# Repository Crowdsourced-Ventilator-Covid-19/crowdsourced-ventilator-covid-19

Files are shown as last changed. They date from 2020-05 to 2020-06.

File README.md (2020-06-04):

# crowdsourced-ventilator-covid-19
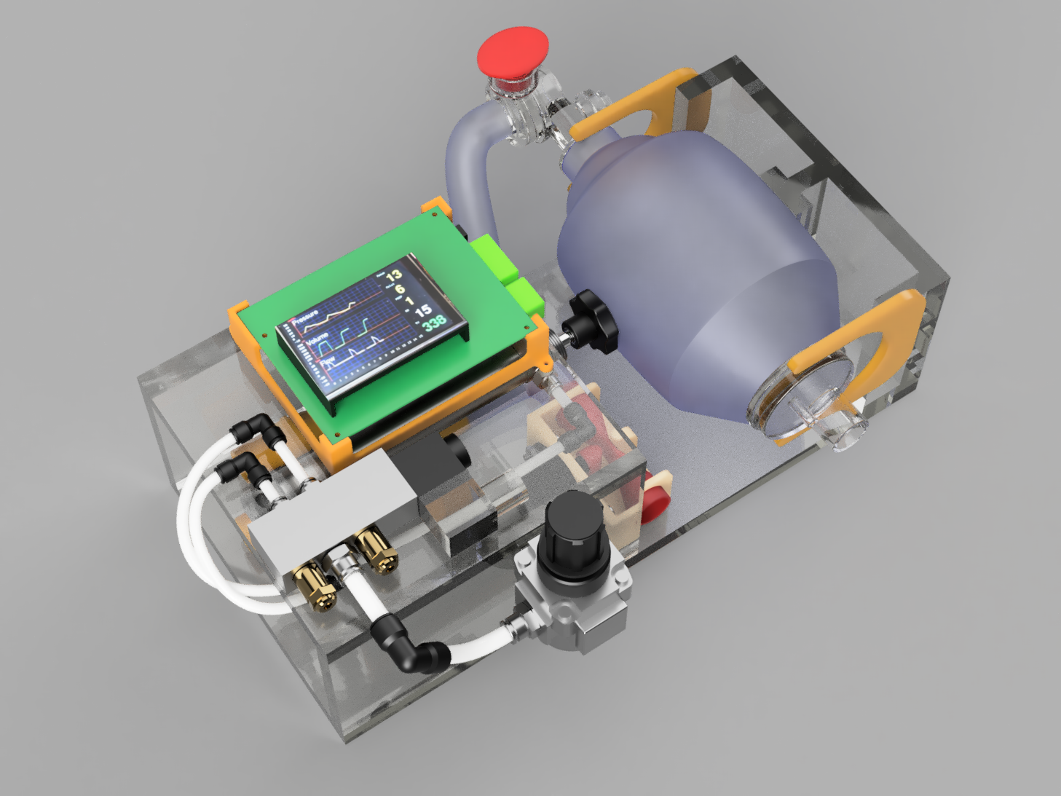
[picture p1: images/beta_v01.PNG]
beta render

## Problem Statement
How to create a safe ventilator that can be used as a last resort where a physician has no choice but to use it or lose a life.  Obviously it will not be FDA approved.  In fact, a wonderful outcome would be if somehow US industry could step up to solve the problem of the ventilator shortage.  However, based on the data we are seeing from Johns Hopkins site above it is likely by the time industry succeeds thousand of people may be in respiratory distress,  particularly in New York City and other big hot spots.  So far no deaths in MA but statistically speaking this will not last for long.

Can we make a difference?
> Honestly I am not sure we can,  but we can try to help, even if we save one life long enough to get on a commercially available ventilator.  In my religion, it is said that saving one life saves an entire world.
-- Joe Siegel

So can we design a ventilator good enough to help and do no harm to the patient?   Can this design be simple enough to put together from components readily available on Amazon or hobby shops or any place that can source the components.  Can we crowd source the production of this design and the cost to build it.  If it can be simple, crowd sourced and done quickly we might be able to help.  The other option is to take the design to someone who will put them into production until the Medical Industrial Complex takes over.

## Team
1. Joe Siegel - Electrical/Physics Engineer  Advanced Micro Devices
1. Steve Bunes - Engineer/Physics and CEO Rise Time Inc. Chicago
1. Chuck Tung - Electrical Engineer / Mechanical Engineer Advanced Micro Devices
1. Dr. David Kagle - Anesthesiologist Emerson Hospital
1. Kenny House - Biomedical Engineer and currently works for AMD 

## Resources
### Specs
- [UK Rapidly Manufactured Ventilator Spec](https://www.gov.uk/government/publications/coronavirus-covid-19-ventilator-supply-specification/rapidly-manufactured-ventilator-system-specification)
- [Pandemic Ventilator User Requirements](https://docs.google.com/spreadsheets/u/2/d/1XAo2LKQBSAnemD73kKWN7G7QsSLVRSNY9SQNuliBCzY/edit#gid=0)
- [OSCMS Requirements](https://docs.google.com/document/d/15kqUPPI7bYL6dnCetOeDSyE8IG5pHVmtg8Ju4yzGlF8/edit?fbclid=IwAR31p6i7iZhFuL7ejLUs5mz9gmRXWi1kWoOG2wR_Lyqr3UgzaOcz6t2VNlk#heading=h.1pr0nkc86xgg)
- [Ventilator spec](https://drive.google.com/open?id=1mXAS4-lcwsU2nRVF3crRuBIVWJfbnB5P)
### Other Projects
- [OpenSourceCoronavirusProjects](https://github.com/cyborg527/OpenSourceCoronavirusProjects)
- [OpenSourceVentilator](https://opensourceventilator.ie/)
- [MIT design](https://www.fastcompany.com/1661942/mit-students-invent-100-ventilator-for-disaster-zones)
- [Hackaday effort](https://hackaday.com/2020/03/12/ultimate-medical-hackathon-how-fast-can-we-design-and-deploy-an-open-source-ventilator/)
### Dashboards
- [Johns Hopkins dashboard](https://gisanddata.maps.arcgis.com/apps/opsdashboard/index.html#/bda7594740fd40299423467b48e9ecf6)
- [Live Interactive dashboard](https://datastudio.google.com/embed/reporting/f56febd8-5c42-4191-bcea-87a3396f4508/page/k1XIB)
- [Epidemic Calculator](http://gabgoh.github.io/COVID/index.html)
- [JHU Time Series Dataset](https://github.com/CSSEGISandData/COVID-19/tree/master/csse_covid_19_data)
### Other
- [Mechanical Ventilation video series](https://www.youtube.com/watch?v=i6hmGVBbIJk)
- [Open Source Medical Supplies Facebook Group](https://www.facebook.com/groups/670932227050506/post_tags/?post_tag_id=674736673336728)
- [A low oxygen consumption pneumatic ventilator for emergency construction during a respiratory failure pandemic - Williams](https://l.facebook.com/l.php?u=https%3A%2F%2Flookaside.fbsbx.com%2Ffile%2FWilliams_et_al-2010-Anaesthesia.pdf%3Ftoken%3DAWx69kPx0nI5HEpVeaNy24bn4q1GDzC0sXTHRSZhE5KIxPyQ67eEu4S7N0iHn_JngGeEK6sNljjXqsA0bA2tAop5FZhIAJotbVWZG8MHPUSA61l7TgDelxZyH2fv6vmKNmL1gULxPK_-b8P3h3ojDA-C_5E6aT0WHfSQDe-etnz0yQ&h=AT3qvgoCUalOjiZATD5rFSJ50BaXUBusOQzW24deVutMAoYmEEW2gb7SYGIeyHJHv5q-TYAeBxpWslhvpChvipB0kV3w04YnqNlw6mtW9Ulel8722b-9MIDKZM1h07lpOwy1N8V3uD4&__tn__=H-R&c[0]=AT2hPfdfSJtkRwnPiZanBKqyTAIH8YzXrv1SWUdh0CvUafrDPVMH3qYw4MAtS64r40eAcNFiGvjK22xvQ87VvWOnltyAbapza0FJKsrX69uNKpJWSq5YWYZUeS-ccZNzSWObEsIWBGhfaV-nHj7KMA)
- [snubber design](https://www.cde.com/resources/technical-papers/design.pdf)
- [easydriver stepper controller](http://www.schmalzhaus.com/EasyDriver/index.html)

## Scope (Tentative pending clarification)
- Required Scope
  - Simple assembly with readily available parts
  - AC Mode in both VCV and PCV
  - TV Control
  - Rate Control
  - I:E Ratio
  - PEEP Control
  - Fio2
  - disconnect alarm
  - inspiratory and expiratory pressure alarm
  - Patient trigger capability
  - humidity and temperature from HME
  - exhaust filter through HME
  - Flow and volume sensing
- Stretch goals
  - Pressure data logging?
- Not POR
  - PC mode

## Proposed usage model
- TV, I/E ratio, RR, Ppeak alarm and Pplat alarm will be set using TFT touch screen
- PEEP setting will be adjusted using a standard adjustable PEEP valve, using graphical UI pressure chart for feedback
- Peak pressure will be adjusted using the compressed air regulator and graphical UI pressure chart for feedback
- Max flow rate and Tp is adusted with the adjustable speed exhaust filter
- FIO2 control is done by matching the O2 flow rate to the specified TV and RR, or a venturi valve premixed supply
- Detect pressure drop below PEEP to trigger patient assisted, and reset breath countdown timer
- Graphical UI will report:
  - Ppeak (peak measured pressure during inspiratory phase)
  - Pplat (final pressure at end of post-inspiratory pause)
  - PEEP (expiratory pressure when DP/DT drops below threshold)

## BOM

| Item | Price |
| --- | --- |
| [HiLetGo ESP32 Dev Kit](https://www.amazon.com/gp/product/B0718T232Z/ref=ppx_yo_dt_b_search_asin_title?ie=UTF8&psc=1) | $11 |
| [AdaFruit 3.5" TFT w/Touch](https://www.adafruit.com/product/2050) | $40 |
| [I2C level shifter](https://www.amazon.com/gp/product/B0148BLZGE/ref=ppx_yo_dt_b_search_asin_title?ie=UTF8&psc=1) | $8 |
| [I2c mux](https://www.amazon.com/gp/product/B06XXG5G3L/ref=ppx_yo_dt_b_search_asin_title?ie=UTF8&psc=1) | $8 |
| [EasyDriver Stepper controller](https://www.amazon.com/gp/product/B00WSNZEBM/ref=ppx_yo_dt_b_search_asin_title?ie=UTF8&psc=1) | $7 |
| [Stepper motor](https://www.amazon.com/gp/product/B07TY4BFF2/ref=ppx_yo_dt_b_search_asin_title?ie=UTF8&psc=1) | $9 |
| [7805 voltage regulator](https://www.amazon.com/gp/product/B01M32I31S/ref=ppx_yo_dt_b_search_asin_title?ie=UTF8&psc=1) | $1 |
| 10uf Cap | |
| 100uf Cap | |
| 0.1uf Cap | |
| 3x 10k Ohm resistor | |
| [3x N-channel power mosfet](https://www.amazon.com/gp/product/B07CTF1JVD/ref=ppx_yo_dt_b_search_asin_title?ie=UTF8&psc=1) | |
| [5way 2pos solenoid](https://www.amazon.com/Baomain-Pneumatic-Solenoid-Internally-Electrical/dp/B01J3CE3EE/ref=sr_1_4?crid=1K7DOXGGJAF8T&dchild=1&keywords=5+way+2+position+pneumatic+valve&qid=1586062215&sprefix=5-way+2+pos%2Caps%2C159&sr=8-4) | $12 |
| [20mm Bore 100mm stroke pneumatic cylinder](https://www.amazon.com/Sydien-Pneumatic-Cylinder-Connector-MAL20X100/dp/B07J9V84VH/ref=sr_1_2?dchild=1&keywords=pneumatic+cylinder+100mm&qid=1586062300&sr=8-2) | $14 |
| [6mm to 1/4" NPT push connects](https://www.amazon.com/TOUHIA-Pneumatic-Straight-Connect-Fittings/dp/B07RXVQPH6/ref=sr_1_4?crid=2NKU48K7C26S9&dchild=1&keywords=1%2F4+npt+push+to+connect+fittings&qid=1586062414&sprefix=1%2F4+npt+pu%2Caps%2C154&sr=8-4) | $8 |
| [Pressure regulator](https://www.amazon.com/Primefit-CR1401G-Replacement-Regulator-steel-Protected/dp/B00IDCYIJ6/ref=sr_1_2?dchild=1&keywords=pressure+regulator&qid=1586062545&sr=8-2) | $6 |
| [Adjustable silencers](https://www.amazon.com/uxcell-Adjustable-Pneumatic-Exhaust-Silencer/dp/B07K39R9Y3/ref=sr_1_2?dchild=1&keywords=pneumatic+adjustable+silencer+1%2F4+npt&qid=1586062735&sr=8-2) | $8 |
| [6mm tubing](https://www.amazon.com/Uxcell-a13080200ux0301-Blue-29-5Ft-Polyurethane/dp/B00G9JQ2JY/ref=sr_1_5?crid=366JZUYPHKWGG&dchild=1&keywords=6mm+pneumatic+tubing&qid=1586062852&sprefix=6mm+pnu%2Caps%2C154&sr=8-5)  | $8 |
| [Teflon tape](https://www.amazon.com/Dixon-Valve-TTB75-Industrial-Temperature/dp/B003D7K8E0/ref=sr_1_8?dchild=1&keywords=teflon+tape&qid=1586097443&sr=8-8) | $2 |
| [3x Differential Pressure Sensor](https://ncd.io/differential-pressure-sensor-arduino/) | 3x $60 |
| [1/8" ID tubing](https://www.amazon.com/gp/product/B0861X9BJT/ref=ppx_yo_dt_b_asin_title_o04_s00?ie=UTF8&psc=1) | $9 |
| [2.5mm ID tubing](https://www.amazon.com/gp/product/B010V5GMEG/ref=ppx_yo_dt_b_asin_title_o04_s01?ie=UTF8&psc=1) | $6 |
| [Tower light and alarm](https://www.adafruit.com/product/2994) | $25 |
| [2x 1N4004 diode](https://www.sparkfun.com/products/14884)| $1 |
| [2x Venturi flow meter tube](https://www.thingiverse.com/thing:4354501) |  |
| [2x PEEP valve](https://www.amazon.com/gp/product/B00Q0SBGR2/ref=ppx_yo_dt_b_search_asin_title?ie=UTF8&psc=1) | $24 |
| Total | $387 |

## Prototype Phase
- Design

v0.03
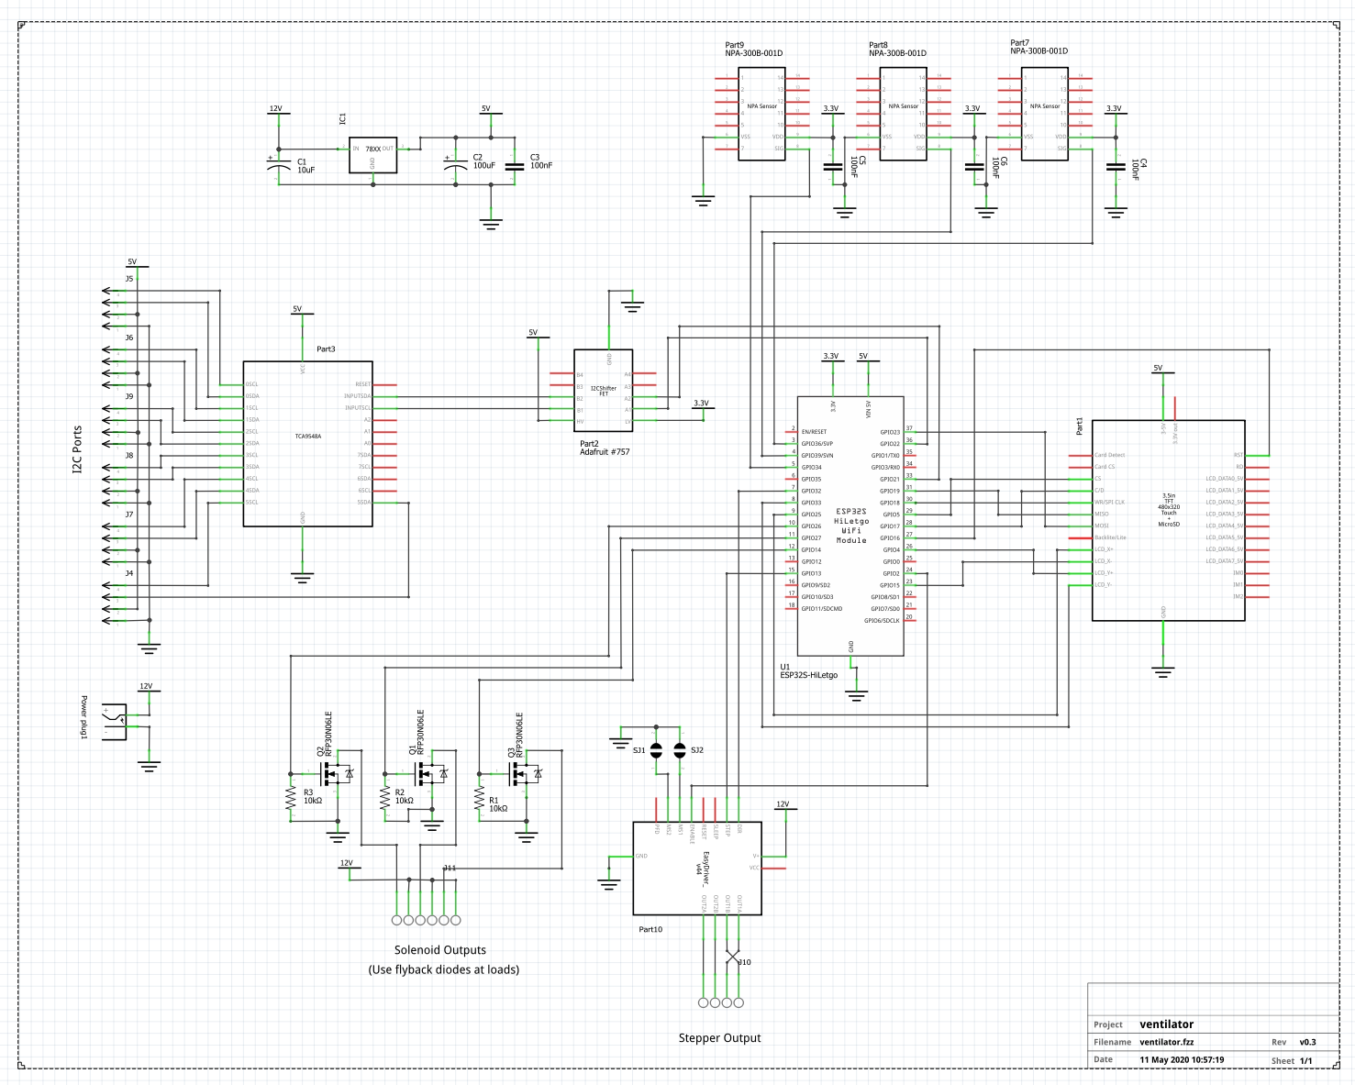
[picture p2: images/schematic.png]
schematic

PCB

- Demonstration
UI demo (https://www.youtube.com/watch?v=sNcdRJmJqwU)
- Patient Assist
AC (https://www.youtube.com/watch?v=ghMTBimfM2k)
- Adjustable pop-off safety
PopOff (https://www.youtube.com/watch?v=k4BQMlsufNU)
- 3d printed Expiratory Valve
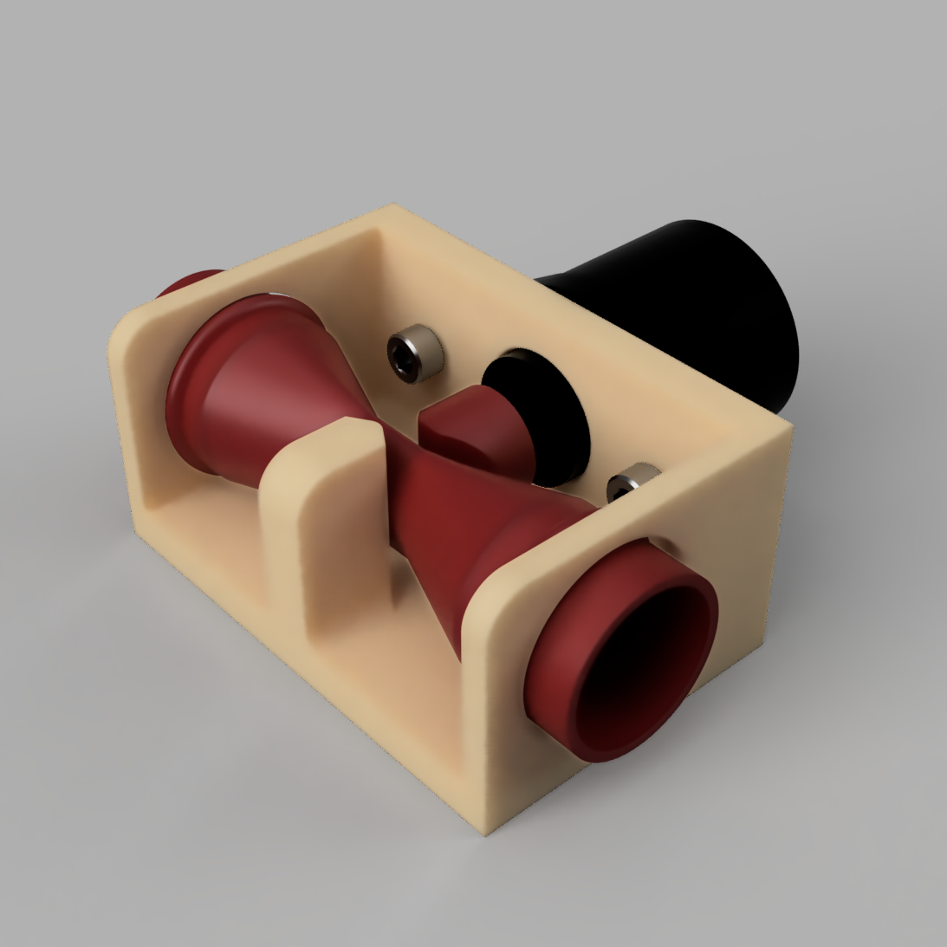
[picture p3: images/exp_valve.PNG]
ev

- Software control flowchart
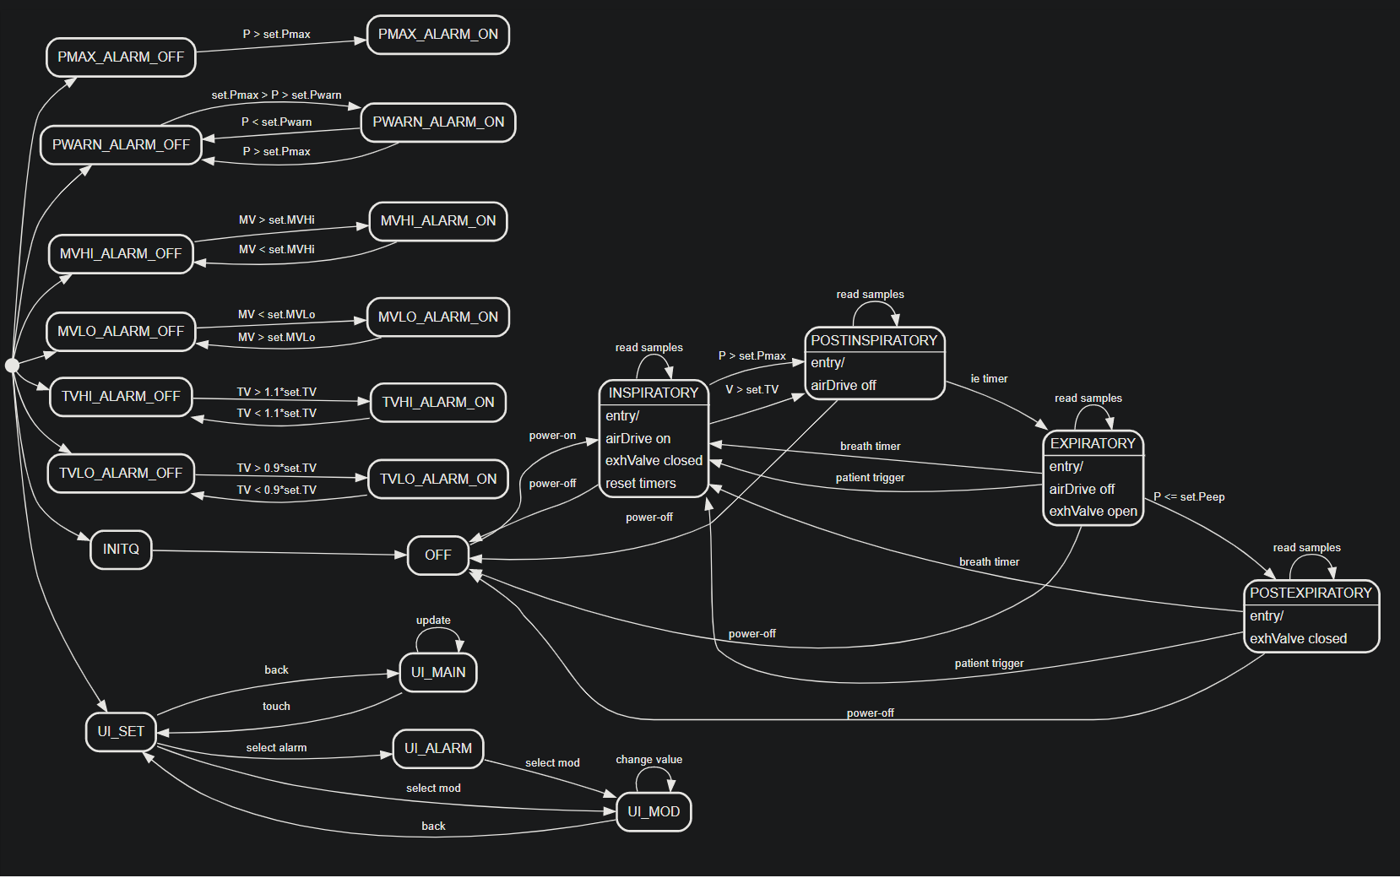
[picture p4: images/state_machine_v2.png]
flowchart


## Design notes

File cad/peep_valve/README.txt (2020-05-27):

Original model: https://www.tinkercad.com/things/2CkW6T01c5j-assembly

print nut_hole at 100% infill merged with cover at any infill
print gasket with TPU
Spring is from lowes hardware store

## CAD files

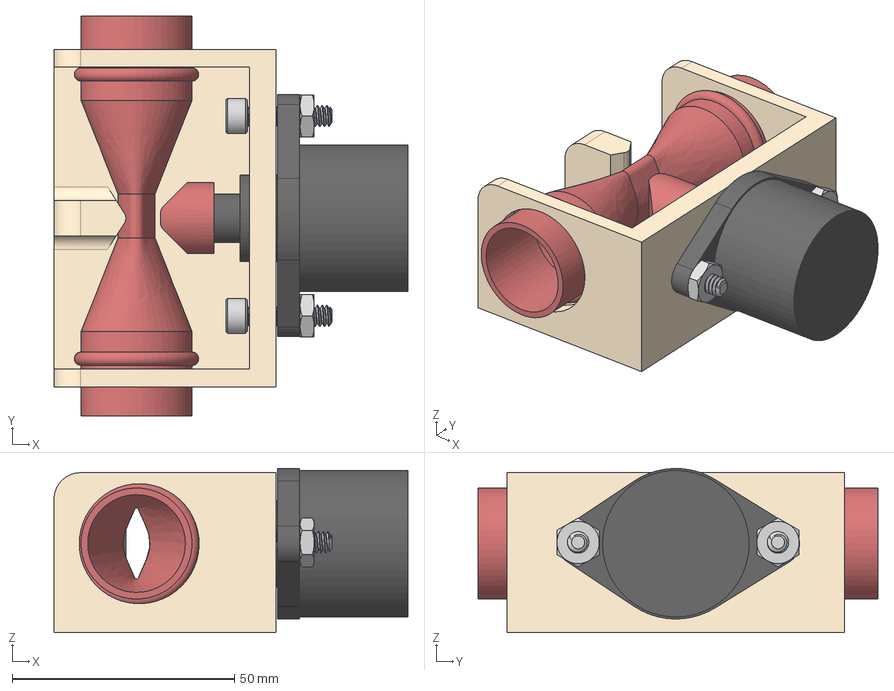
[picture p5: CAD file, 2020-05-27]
cad/exhalation_valve/iac assembly v3.step
79.7 x 90.0 x 36.9 mm
iac
piston cap
tube
frame
90128A222 x 2
90480A011 x 2

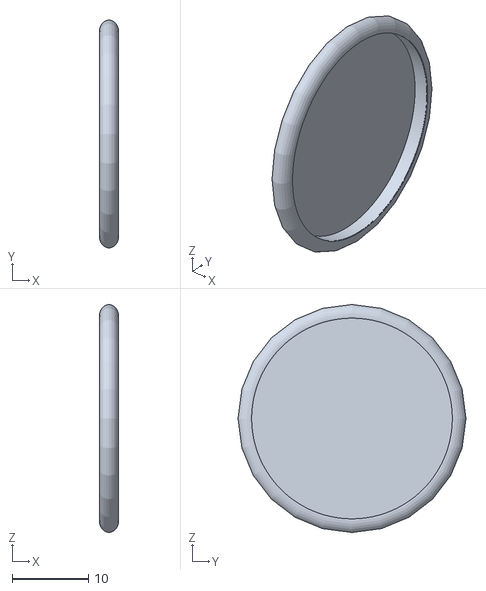
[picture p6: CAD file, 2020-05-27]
cad/peep_valve/gasket.stl
2.51 x 30.0 x 30.0

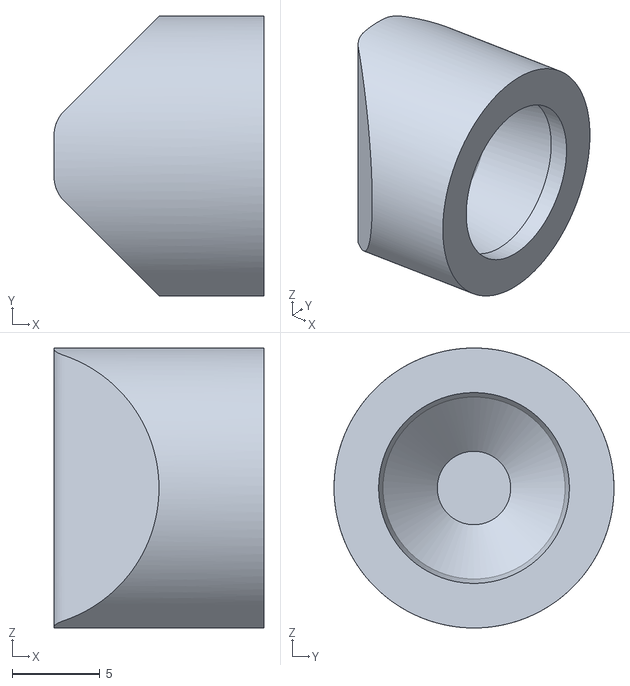
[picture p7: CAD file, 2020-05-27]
cad/exhalation_valve/piston cap.stl
12.0 x 16.0 x 16.0

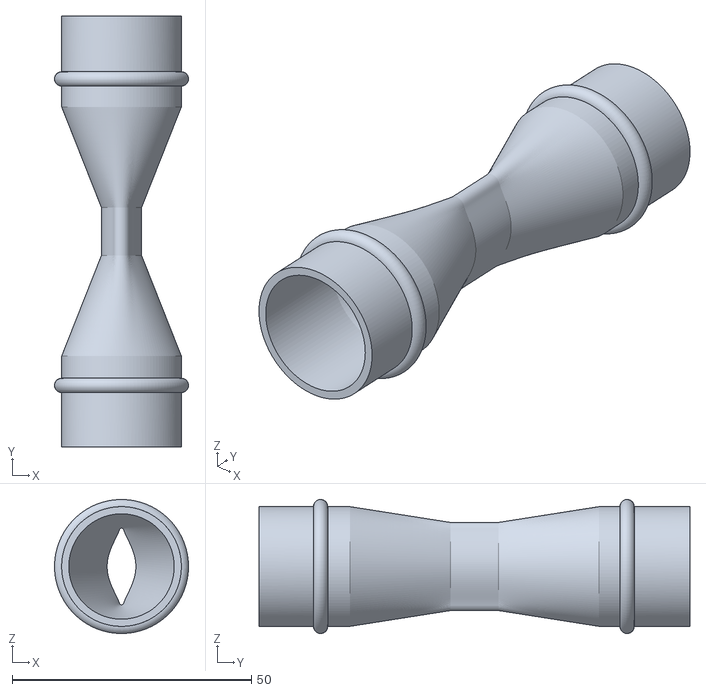
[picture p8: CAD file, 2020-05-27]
cad/exhalation_valve/tube.stl
28.0 x 90.0 x 28.0

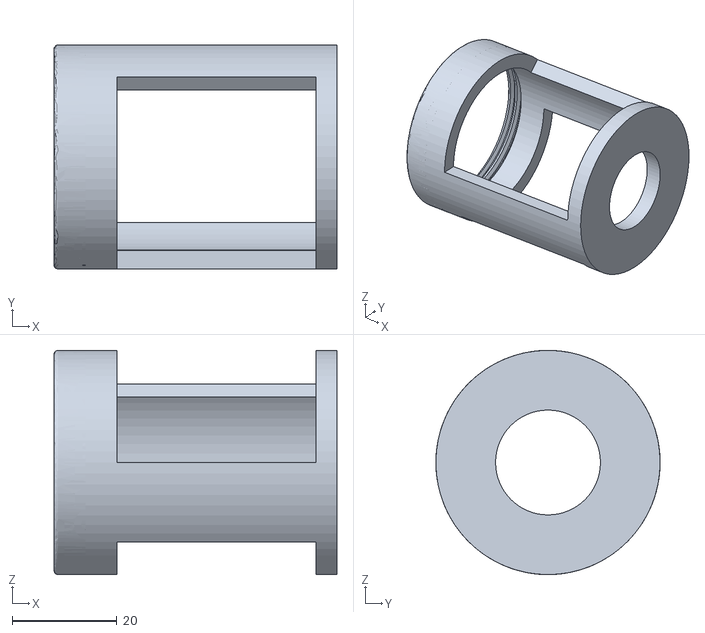
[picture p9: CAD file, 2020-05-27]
cad/peep_valve/cover.stl
54.0 x 42.8 x 42.8

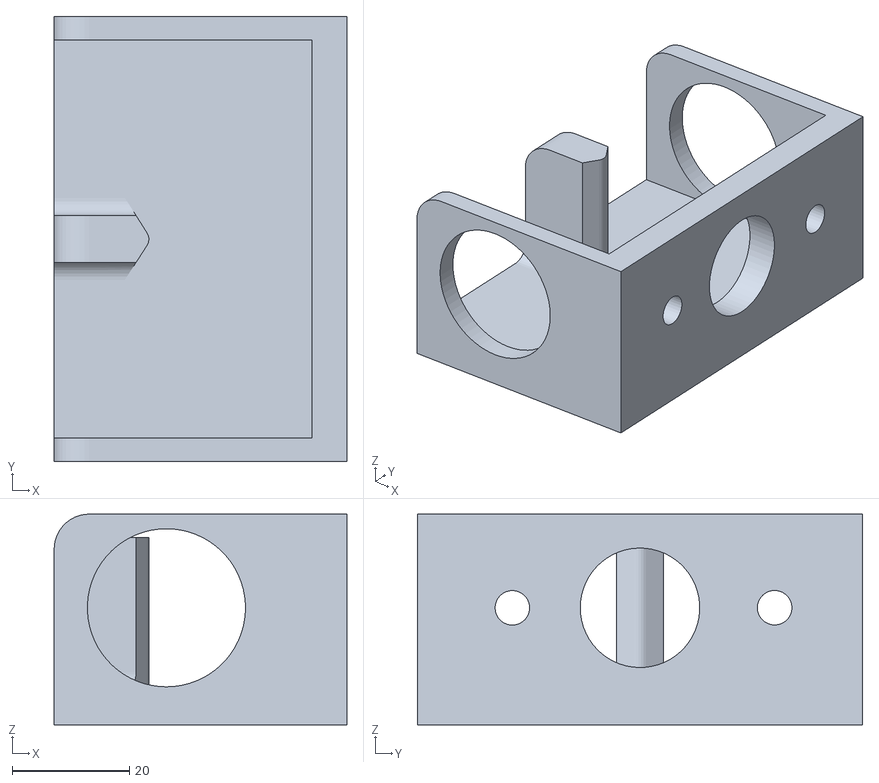
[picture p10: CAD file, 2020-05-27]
cad/exhalation_valve/frame.stl
50.0 x 76.0 x 36.0

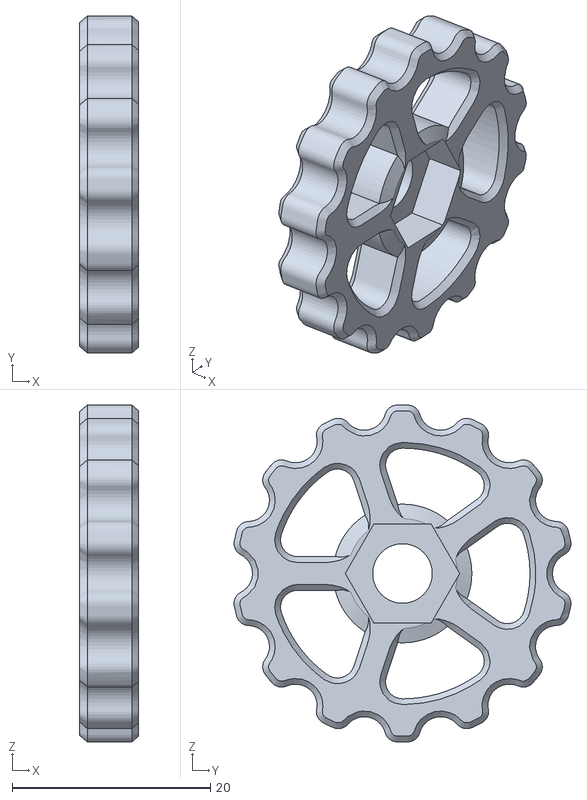
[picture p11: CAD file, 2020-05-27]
cad/peep_valve/knob.stl
6.00 x 34.0 x 34.0

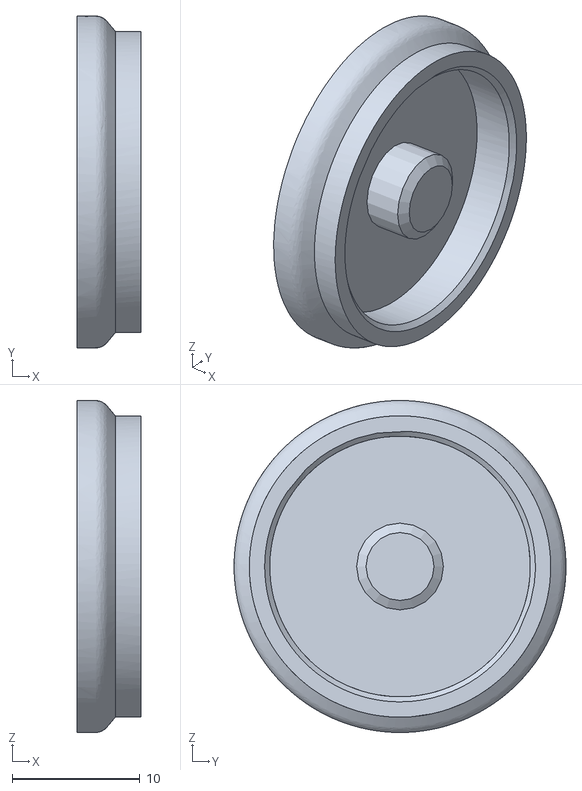
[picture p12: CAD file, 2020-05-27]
cad/peep_valve/piston.stl
5.00 x 26.0 x 26.0

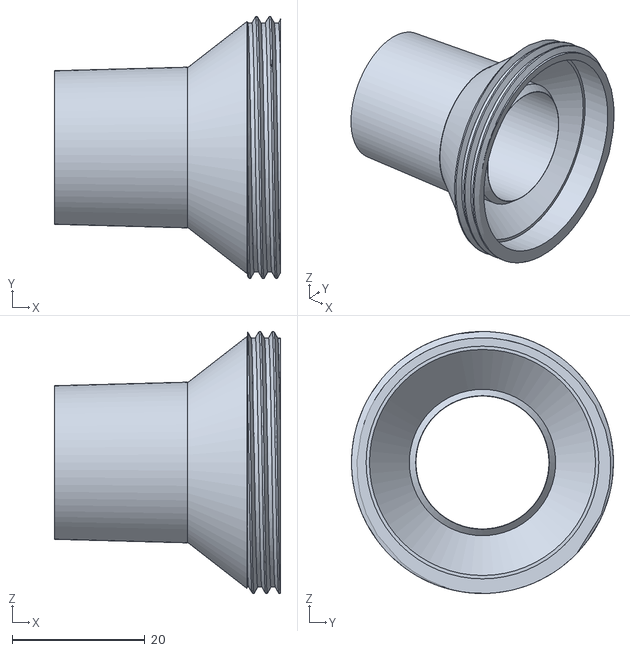
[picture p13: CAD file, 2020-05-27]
cad/peep_valve/base.stl
34.0 x 39.4 x 39.4

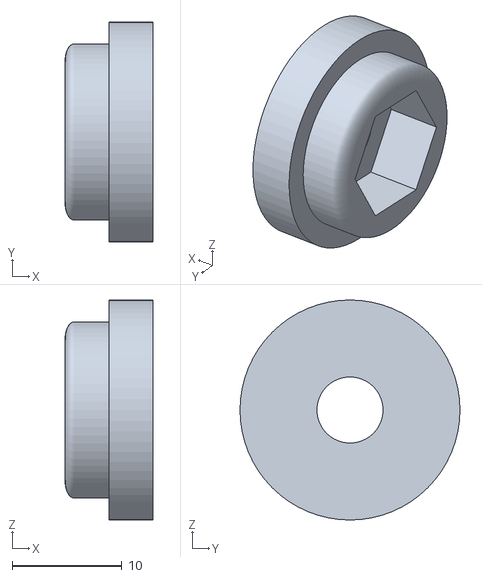
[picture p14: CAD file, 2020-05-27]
cad/peep_valve/nut_hole.stl
8.00 x 20.0 x 20.0

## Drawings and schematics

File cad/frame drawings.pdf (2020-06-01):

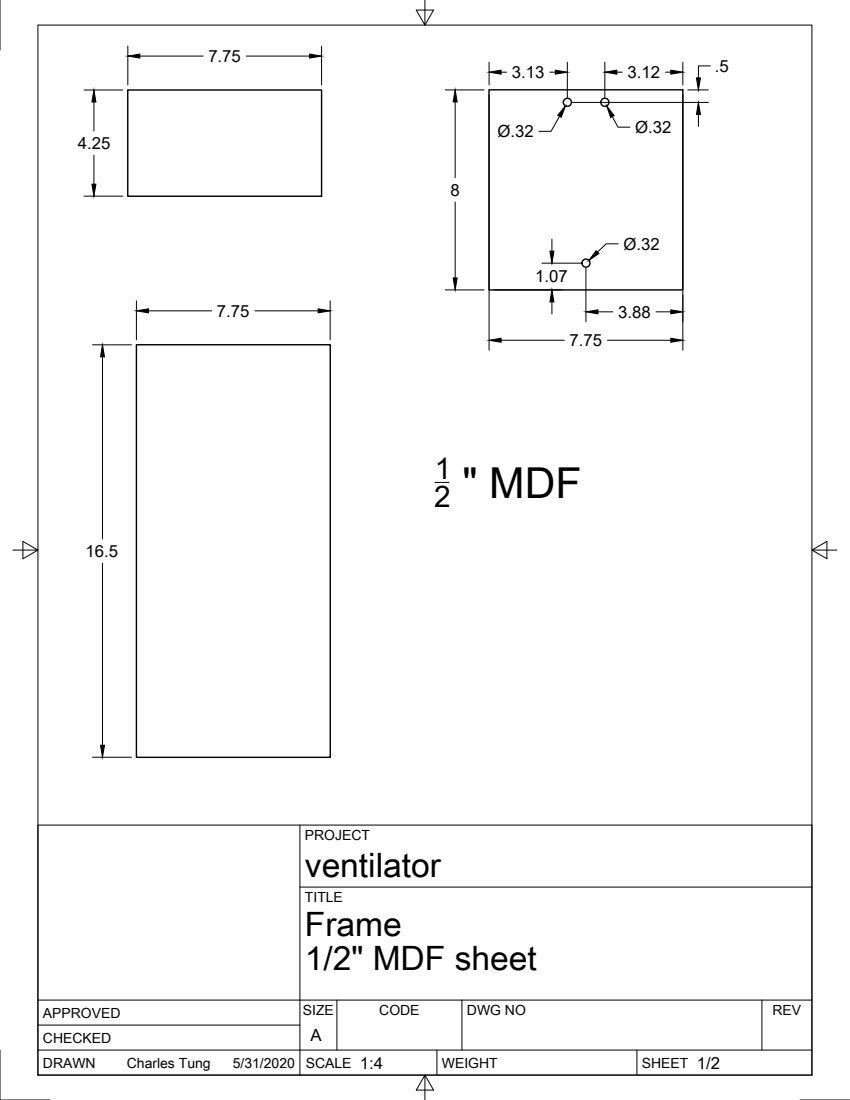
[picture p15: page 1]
SIZE; CODE; DWG NO; REV; Charles Tung; 1/2" MDF sheet; " MDF

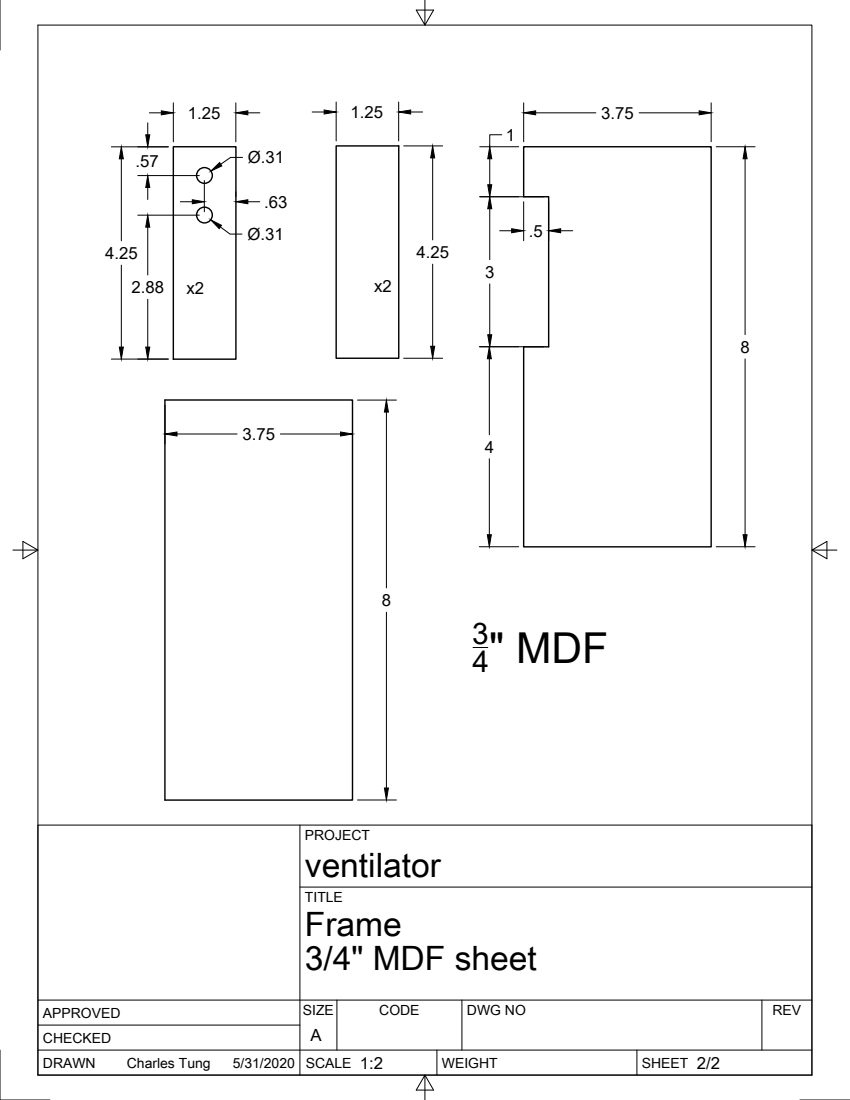
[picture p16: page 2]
SIZE; CODE; DWG NO; REV; Charles Tung; 3/4" MDF sheet; 3/4" MDF

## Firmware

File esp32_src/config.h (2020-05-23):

#ifndef config_h
#define config_h

#define PISTON 14
#define EXPVALVE 27
#define ALARM 26
#define STEP_DIR 32
#define STEP_STEP 13
#define STEP_EN 2

// These are the four touchscreen analog pins
#define YP A10  // must be an analog pin, use "An" notation!
#define XM A13  // must be an analog pin, use "An" notation!
#define YM 33    // can be a digital pin
#define XP 25   // can be a digital pin

// This is calibration data for the raw touch data to the screen coordinates
#define TS_MINX 120
#define TS_MINY 90
#define TS_MAXX 940
#define TS_MAXY 959
#define MINPRESSURE 10
#define MAXPRESSURE 1000

// The display uses hardware SPI, plus #9 & #10
#define TFT_RST -1  // dont use a reset pin, tie to arduino RST if you like
#define TFT_DC 17
#define TFT_CS 5
#define RESET_PIN -1
#define EOC_PIN -1

#define LTBLUE    0xB6DF
#define LTTEAL    0xBF5F
#define LTGREEN   0xBFF7
#define LTCYAN    0xC7FF
#define LTRED     0xFD34
#define LTMAGENTA 0xFD5F
#define LTYELLOW  0xFFF8
#define LTORANGE  0xFE73
#define LTPINK    0xFDDF
#define LTPURPLE  0xCCFF
#define LTGREY    0xE71C

#define BLUE      0x001F
#define TEAL      0x0438
#define GREEN     0x07E0
#define CYAN      0x07FF
#define RED       0xF800
#define MAGENTA   0xF81F
#define YELLOW    0xFFE0
#define ORANGE    0xFC00
#define PURPLE    0x8010
#define GREY      0xC618
#define WHITE     0xFFFF
#define BLACK     0x0000

#define DKBLUE    0x000D
#define DKTEAL    0x020C
#define DKGREEN   0x03E0
#define DKCYAN    0x03EF
#define DKRED     0x6000
#define DKMAGENTA 0x8008
#define DKYELLOW  0x8400
#define DKORANGE  0x8200
#define DKPINK    0x9009
#define DKPURPLE  0x4010
#define DKGREY    0x4A49

#define flowDeadZone 3  // ignore flow below 3lpm
#endif

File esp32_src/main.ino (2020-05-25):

#define SIM_LUNG   // use this to run simulated sensors

#define ARDUINO 10812
#include <Arduino.h>
#include <Adafruit_GFX.h>    // Core graphics library
#include <Adafruit_HX8357.h>
#include <TouchScreen.h>
#include <SPI.h>
#include "Wire.h"

// defines, structs and enums
#include "config.h"
#include "types.h"

// screens
#include "set_screen.h"
#include "main_screen.h"
#include "mod_screen.h"
#include "alarm_screen.h"

// sensor classes
#ifdef SIM_LUNG
#include "sim_lung.h"
#include "sim_psens.h"
#include "sim_fsens.h"
#else
#include "psens.h"
#include "fsens.h"
#endif

#include "AccelStepper.h"

// tft screen
Adafruit_HX8357 tft = Adafruit_HX8357(TFT_CS, TFT_DC, TFT_RST);
// For better pressure precision, we need to know the resistance
// between X+ and X- Use any multimeter to read it
// For the one we're using, its 300 ohms across the X plate
TouchScreen ts = TouchScreen(XP, YP, XM, YM, 300);

#ifdef SIM_LUNG
// these are simulated sensors for testing without hardware
QueueHandle_t lungQ = xQueueCreate(1, sizeof(Lung_t));  // sim lung
SimPsens psens = SimPsens(lungQ, 1);
SimFsens iFsens = SimFsens(lungQ, 0);
SimFsens eFsens = SimFsens(lungQ, 2);
#else 
// these are the real sensors
Psens psens = Psens(1);   // pressure sensor
Fsens iFsens = Fsens(0);  // inspiratory flow sensor
Fsens eFsens = Fsens(2);  // expiratory flow sensor
#endif

// queuehandles
QueueHandle_t sampleQ = NULL;   // hold sensor readings in 1000 deep queue
QueueHandle_t settingQ = NULL;  // configurable settings, 1 deep queue
QueueHandle_t stateQ = NULL;    // state, 1 deep queue
QueueHandle_t alarmQ = NULL;    // alarm conditions, 1 deep queue

// set this 60s into the future when alarm mute button is pressed
unsigned long alarmMuteTimer = 0;

void setup(void) {
    Wire.begin();
    Serial.begin(115200);

    tft.begin();
    tft.setRotation(3);
    tft.fillScreen(BLACK);

    // calibrate the sensors
    psens.calibrate(tft);
    iFsens.calibrate(tft);
    eFsens.calibrate(tft);
    delay(5000);

    // initialize the queues
    initQ();

    // place timing critical tasks on core 0, and all other non timing critical tasks on core 1
    xTaskCreatePinnedToCore(
                    readSensor,          /* Task function. */
                    "ReadSensor",        /* String with name of task. */
                    10000,            /* Stack size in bytes. */
                    NULL,             /* Parameter passed as input of the task */
                    1,                /* Priority of the task. */
                    NULL,             /* Task handle. */
                    0);               /* pin to core 0 */

    #ifdef SIM_LUNG
    xTaskCreatePinnedToCore(
                    simLung,          /* Task function. */
                    "SimLung",        /* String with name of task. */
                    10000,            /* Stack size in bytes. */
                    NULL,             /* Parameter passed as input of the task */
                    1,                /* Priority of the task. */
                    NULL,             /* Task handle. */
                    0);               /* pin to core 0 */
    #endif

    xTaskCreatePinnedToCore(
                    displayResults,          /* Task function. */
                    "DisplayResults",        /* String with name of task. */
                    10000,            /* Stack size in bytes. */
                    NULL,             /* Parameter passed as input of the task */
                    1,                /* Priority of the task. */
                    NULL,             /* Task handle. */
                    1);               /* pin to core 1 */

    xTaskCreatePinnedToCore(
                    alarmTask,          /* Task function. */
                    "alarmTask",        /* String with name of task. */
                    10000,            /* Stack size in bytes. */
                    NULL,             /* Parameter passed as input of the task */
                    1,                /* Priority of the task. */
                    NULL,             /* Task handle. */
                    1);               /* pin to core 1 */

    xTaskCreatePinnedToCore(
                    exhValveTask,          /* Task function. */
                    "exhValveTask",        /* String with name of task. */
                    10000,            /* Stack size in bytes. */
                    NULL,             /* Parameter passed as input of the task */
                    1,                /* Priority of the task. */
                    NULL,             /* Task handle. */
                    1);               /* pin to core 1 */

    xTaskCreatePinnedToCore(
                    airDriveTask,          /* Task function. */
                    "airDriveTask",        /* String with name of task. */
                    10000,            /* Stack size in bytes. */
                    NULL,             /* Parameter passed as input of the task */
                    1,                /* Priority of the task. */
                    NULL,             /* Task handle. */
                    1);               /* pin to core 1 */
}

void loop() {
    delay(1000);
}


// monitor for alarms and flash the alarm if needed
void alarmTask( void * parameter) 
{   
    Alarm_t alarms;
    alarmMuteTimer = 0;
    unsigned long pulseTimer = 0;
    int alarmState = LOW;
    pinMode(ALARM, OUTPUT);
    digitalWrite(ALARM, LOW);

    for (;;) {
        xQueuePeek(alarmQ, &alarms, 10);
        if ((millis() > alarmMuteTimer) && (alarms.pmax || alarms.pwarn || alarms.mvhi || alarms.mvlo || alarms.dc) && (millis() > pulseTimer)) {
            alarmState = !alarmState;
            digitalWrite(ALARM, alarmState);
            pulseTimer = millis() + 1000;
        } else {
            digitalWrite(ALARM, LOW);
        }
        delay(100);
    }
}

// read sensor
void readSensor( void * parameter )
{
    Sample_t sample;
    uint32_t ieTimer = 0;
    uint32_t breathTimer = 0;
    State_t state;
    Settings_t settings;
    Alarm_t alarms;
    float v;
    breathTimer = 0;
    ieTimer = 0;

    for(;;) {
        xQueuePeek(stateQ, &state, 10);
        xQueuePeek(settingQ, &settings, 10);
        xQueuePeek(alarmQ, &alarms, 10);

        // read patient pressure & timestamp
        psens.read();
        sample.p = psens.p;
        sample.p_ts = psens.t;

        if (psens.p > settings.pmax) {
            // exceeded hard pressure ceiling, retract piston, fire alarm
            if(state.phase == INSPIRATORY) {
                state.phase = POSTINSPIRATORY;
                xQueueOverwrite(stateQ, &state);
            }
            alarms.pmax = true;
            alarms.pwarn = false;  // overwrite soft warning
            xQueueOverwrite(alarmQ, &alarms);
        } else if (psens.p > settings.peakAlarm) {
            // exceeded soft pressure warning threshold, fire alarm
            alarms.pwarn = true;
            xQueueOverwrite(alarmQ, &alarms);
        }

        switch(state.phase) {
            case EXPIRATORY:
                eFsens.read();
                iFsens.read();
                sample.f = iFsens.f - eFsens.f;
                sample.f_ts = eFsens.t;
                sample.v = v +iFsens.v - eFsens.v;
                sample.v_ts = eFsens.t;

                // if time for a new breath or if patient tried to inhale
                if (millis() > breathTimer || (settings.trig > 0 && iFsens.v > settings.trig))  {
                    state.phase = INSPIRATORY;
                    state.peep = psens.p;       // capture PEEP at end of expiratory phase
                    psens.peak = 0;             // reset peak pressure tracker
                    eFsens.v = 0;               // reset expiratory flow meter
                    xQueueOverwrite(stateQ, &state);

                    // reset timer
                    breathTimer = round(60.0 / settings.rr * 1000.0) + millis();
                    ieTimer = round((60.0 / settings.rr * 1000.0) * (1.0 - (float(settings.ier)/10.0 / (float(settings.ier)/10.0+1.0)))) + millis();
                }
                break;
            default: // INSPIRATORY or POSTINSPIRATORY
                iFsens.read();
                // read inspiratory flow
                sample.f = iFsens.f;
                sample.f_ts = iFsens.t;
                // read inspiratory volume
                sample.v = iFsens.v;
                sample.v_ts = iFsens.t;

                // TODO: add DC alarm looking for failure for pressure to increase
                // TODO: add DC alarm looking for expiratory volumn difference from inspiratory

                // check if we've hit desired TV
                if (state.phase == INSPIRATORY && iFsens.v >= settings.tv) {
                    state.phase = POSTINSPIRATORY;
                    xQueueOverwrite(stateQ, &state);
                }

                if (millis() > ieTimer) {
                    // retract piston, open expiratory valve
                    iFsens.updateMv();          // update minute volume tracker
                    state.phase = EXPIRATORY;
                    state.peak = psens.peak;    // report peak pressure during inspiratory phase
                    state.plat = psens.avg;     // log avg of last 10 samples as plateau pressure
                    state.tv = iFsens.v;        // log tidal volume delivered during inspiratory phase
                    state.minvol = iFsens.mv;   // log minute volume
                    alarms.mvhi = (iFsens.mv / 1000.0 > settings.mvhiAlarm);    // set alarms for minute volume
                    alarms.mvlo = (iFsens.mv / 1000.0 < settings.mvloAlarm);
                    state.rr = iFsens.rr;       // log the actual respiratory rate
                    v = iFsens.v;               // save off delivered tidal volume
                    iFsens.v = 0;               // reset insp flow meter to look for patient trigger

                    // TODO: add PEEP alarm
                    xQueueOverwrite(stateQ, &state);
                    xQueueOverwrite(alarmQ, &alarms);
                }
                break;
        }
        if(xQueueSend(sampleQ, &sample, 0) != pdTRUE) {
            Serial.println("queue error\n\r");
        }
        delay(10);
    }
}
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

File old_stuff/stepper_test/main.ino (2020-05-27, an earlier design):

#include <Arduino.h>
#define ARDUINO 10812
#include "AccelStepper.h"

#define STEP_DIR 32
#define STEP_STEP 13
#define STEP_EN 2


int Distance = 0;

void setup() {               
  pinMode(STEP_DIR, OUTPUT);    
  pinMode(STEP_STEP, OUTPUT);
  pinMode(STEP_EN, OUTPUT);
  digitalWrite(STEP_DIR, LOW);
  digitalWrite(STEP_STEP, LOW);
  digitalWrite(STEP_EN, LOW);
}

void loop() {
  digitalWrite(STEP_STEP, HIGH);
  delayMicroseconds(2000);         
  digitalWrite(STEP_STEP, LOW);
  // delayMicroseconds(1000);
  Distance = Distance + 1;   // record this step
 
  // Check to see if we are at the end of our move
  if (Distance == 120)
  {
    // We are! Reverse direction (invert DIR signal)
    if (digitalRead(STEP_DIR) == LOW)
    {
      digitalWrite(STEP_DIR, HIGH);
    }
    else
    {
      digitalWrite(STEP_DIR, LOW);
    }
    // Reset our distance back to zero since we're
    // starting a new move
    Distance = 0;
    // Now pause for half a second
    delay(500);
  }
}

/*
AccelStepper stepper(AccelStepper::DRIVER, STEP_STEP, STEP_DIR);
int pos = 65;

void setup()
{ 
    stepper.setEnablePin(STEP_EN);
    stepper.setPinsInverted(false,false,true);
    stepper.setMaxSpeed(9000);
    stepper.setAcceleration(7000);
}

void loop()
{
    stepper.enableOutputs();
  if (stepper.distanceToGo() == 0)
  {
    delay(500);
    pos = -pos;
    stepper.moveTo(pos);
  }
  stepper.run();
}
*/

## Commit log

2020-04-01 Initial pressure graphing on TFT
2020-04-17 fix boot bug
    AMS5915 will sometimes return NAN, and if that happens during calibration, all future measurements return NAN. loop until I get a good calibration, and add a diag screen to report health
2020-04-18 Create VentSensBoxBtm.stl
    Add stl files for sensor box bottom
    [VentSensBoxBtm.stl]
2020-04-29 add venturi calculations
    [venturi_calcs.xlsx]
2020-04-30 add patient trigger
2020-05-01 add patient triggering
2020-05-11 Add pcb
    [ventilator.fzz]
2020-05-11 update schematic
    [ventilator.fzz]
2020-05-14 move power to settings
2020-05-15 fix copper fill
    [ventilator.fzz]
2020-05-20 add pressure sensor and i2c class
2020-05-23 fix screw terminal holes, missing ground plane
    [ventilator.fzz, ventilator_contour.gm1, ventilator_copperBottom.gbl, ventilator_copperTop.gtl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]
2020-05-23 add stepper driver, move piston to its own task
2020-05-23 Fix stepper.moveTo for open exhValve
2020-05-25 stepper testing
    [ventilator_v0p2.fzz]
2020-05-27 add cad models
    [VentSensBoxBtm.stl, base.stl, cover.stl, frame.stl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]
2020-06-04 board fixes
    add 3.3v power to I2C levelshifter,
    change SDA pin to GPIO21 on ESP32
    [ventilator.fzz, ventilator_v0p3.fzz]
2020-06-04 add new schematic pic
    [ventilator.fzz]
